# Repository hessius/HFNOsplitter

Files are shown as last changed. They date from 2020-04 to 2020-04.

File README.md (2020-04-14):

# Welcome to the HFNOsplitter project - SHFNO.org

This project is dedicated to doubling the capacity for High Flow Nasal Oxygen (HFNO) treatment by simultaneously connecting two COVID-19 patients to one HFNO-device by adding 3D printed parts.
We also provide thorough medical instructions, validation, and risk analysis to enable other healthcare providers to adopt Split HFNO (SHFNO).
This project is currently only aimed at the Airvo™ 2 Optiflow™ system (Fisher & Paykel Healthcare Limited, Berkshire, United Kingdom).

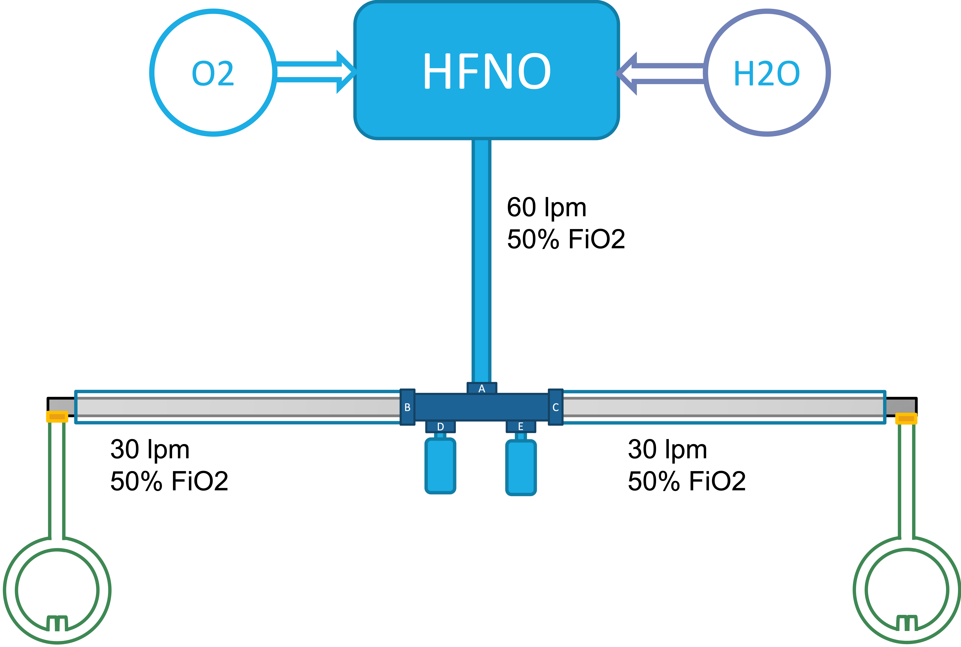
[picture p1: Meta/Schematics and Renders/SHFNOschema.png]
SHFNO Schematic setup

_Fig 1. SHFNO Schematic setup_

**N.B. 1 This solution is provided as is with no express or implied warranty.** [**_Provided under the CERN-OHL-S license_**](https://github.com/hessius/HFNOsplitter/blob/master/LICENSE_cern_ohl_s_v2.pdf).
**In no event will the authors be held liable for any damages arising from the use of this solution.** [**_Legal notice_**](Documentation/en/00%20about%20this%20documentation.html).

**N.B. 2 This project is not done in conjuction or collaboration with, nor under the influence of the original manufacturer of any equipment, medical or otherwise.**

---

## Working group

- **Jesper Hessius**

  - _MD, Internal Medicine and Cardiology Resident_, Västmanland Hospital Västerås Region Västmanland
  - **Role:** Project initiator - Project coordinator - Documentation - Risk analysis

---

- **Erik Cederberg**

  - _Chief Engineer_, 3Dverkstan
  - **Role:** CAD - Design

---

- **Erik Ekbom**

  - _Biomedical Engineer_, Imaging and Functional Technology, Skåne University Hospital Lund
  - **Role:** 3D printing

---

- **Petter Frieberg**
  - _MD, Engineer, PhD-Student_, Clinical Physiology and Nuclear Medicine, Skåne University Hospital Lund
  - **Role:** Validation - Flow simulations

---

- **Einar Heiberg**
  - _Associate Professor, Engineer_, Clinical Physiology, Skåne University Hospital Lund
  - **Role:** 3D printing - Regulatory affairs

---

- **Per Nordqvist**
  - _Biomedical Engineer_, Department of Medical Technology Skåne<br> Region Skåne
  - **Role:** Regulatory affairs - Documentation - Risk analysis

---

- **Göran Petersson**
  - _Biomedical Engineer_, Department of Medical Technology Skåne<br> Region Skåne
  - **Role:** Validation - Documentation

---

## Thanks to

### [3Dverkstan](http://3dverkstan.se) for providing their time, effort, expertise and printers for this project. Without them none of this would have happened.

All the online communities, doctors, nurses and medical technicians who have provided their input and knowledge into every step of this process.

---

## License

**[Provided under the CERN-OHL-S license](https://github.com/hessius/HFNOsplitter/blob/master/LICENSE_cern_ohl_s_v2.pdf).**

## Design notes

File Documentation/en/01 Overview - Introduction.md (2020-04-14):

# Overview

Treating two patients in parallell with High-Flow Nasal Oxygen (HFNO) using the Airvo 2 system is possible due to<br>
a. Treatment guidelines that stipulate a maximum flow should be kept as low as possible to avoid / minimise aerosol dispersion, often capped at 30 lpm.<br>
b. The Airvo 2 system being capable of outputting 60 litres/minute (well above recommended maximum air flow)

Treating two patients in parallell with HFNO using the Airvo 2 system is feasible due to<br>
a. Unidirectional high flow makes cross contamination unlikely<br>
b. Using this only for cohort care with patients with the same disease makes cross contamination less significant<br>
c. HFNO being a completely open system / circuit makes patient factors non significant for air flow dynamics<br>
d. In the authors' limited experience the COVID-19 patients are often titrated to very similar treatments<br>

---

# Basic Schematics

| Standard Setup                                                                                     | SHFNO setup                                                                         |
| -------------------------------------------------------------------------------------------------- | ----------------------------------------------------------------------------------- |
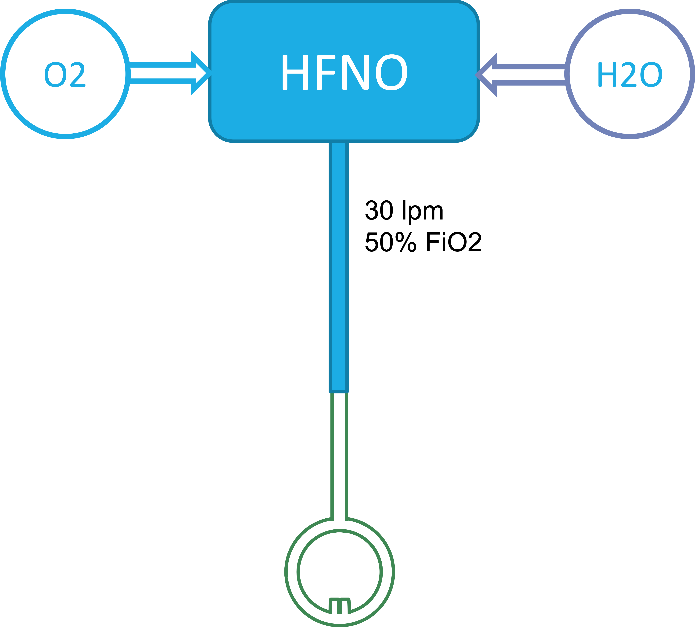
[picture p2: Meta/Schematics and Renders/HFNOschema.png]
Standard HFNO Setup
|  | SHFNO Setup |

---

# Introduction

High-Flow Nasal Oxygen (HFNO) / High Flow Nasal Cannula (HFNC) is a staple of treatment in COVID-19, especially as many countries, regions, hospitals, and health care providers are now recommending against regularly using CPAP and Non-Invasive Ventilation (NIV)/BiPAP in these patients. This is the case in Sweden (where this project was initiated), where the Infectious Diseases Association of Sweden (**IDAS**, "Svenska Infektionsläkarföreningen" in Swedish) has recommended not using CPAP or NIV as well as limited upper maximums for HFNO (See below).

In the best case scenario, used in a timely and correct manner in the context of the COVID-19 pandemic, HFNO/HFNC can be used to avoid intubation and invasive ventilation. However, access to HFNO systems can be severely limited and scarcer than other equipment such as BiPAP machines.

The main system in use outside of the ICU is the Fisher & Paykel Airvo 2, often called "**Optiflow**", which more precisely is the special nasal cannula used with the system. The Airvo is capable of outputting 2-60 litres / minute of airflow with 21-100% FiO2 and uses wholly proprietary connectors which are not readily available and cannot be used with standardised respiratory equipment.

IDAS, as well as the [Karolinska University Hospital](https://strummet.files.wordpress.com/2020/03/pmi-karolinska-covid-19-lungsvikt-intubation-ventilatorbeh-2020-03-19.pdf) both recommend limiting the HFNO air flow in COVID-19 patients to 30 litres / minute due to risk of aeorosolisation and the FiO2 to 50 % due to the risk of alveolar collapse. Some hospitals, like Västmanland Hospital Västerås (where this project orginated), have subsequently modified these guidelines based on clinical experience to allow higher FiO2 as well as in some cases higher air flows. Even so, **the Airvo 2 is _theoretically_ capable of supplying two patients with HFNO without impeding the maximum recommended levels of treatment** according to major guidelines.

HFNO systems are well suited for split airflow, substantially more so than invasive ventilators, CPAP, or BiPAP. This is due to the open nature of the system, which causes patient factors, such as airway resistance to have minimal impact on the air flow. The unidirectionality of the air flow means that no air is shared between patients, even without added filtration. Even so, it is the authors' suggestion that the only patients eligible for treatment with Split HFNO (Hereon "**SHFNO**") are patients suffering from the same disease, such as COVID-19, which also means that potential cross-bcontamination across patients is less significant. We further recommend against using SHFNO for patients with _confirmed_ secondary bacterial infections as well as for carriers of drug-resistant bacteria.

**While every health care provider utilising SHFNO will need to ensure that they have medical instructions for use in place, these guidelines are provided as an example, which is subject to change and without any liability (_[see Legal Disclaimer](00%20about%20this%20documentation.html)_). These examples are based on the medical instructions for use from Västmanland Hospital Västerås, in Sweden where the project originated.**

In the limited clinical experience of the authors, COVID-19 patients treated under the recommendations above are invariably using HFNO titrated to very similar flows and FiO2. For suggestions on how to start treatment with HFNO / SHFNO please see the provided on [**Setup and Treatment**](04%20setup%20and%20treatment.html).

### To enable SHFNO we provide 3D models of

1. A **T-shaped connector** used to connect the distal end of the Airvo connected tube (AirSpiral) with two standard 22mm CPAP/BiPAP tubes as well as two bottles used to collect condensate.
2. An **Adapter** between the distal end of a standard 22mm CPAP/BiPAP tube and the proximal end of the Optiflow nasal cannula.

**A standard SHFNO setup requires one T-shaped connector as well as two adapters.**

It is our recommendation that these models be printed using high quality resin approved for medical use. Please see part 3 of this documentation, [**Models and Instructions**](03%20models%20and%20instructions.html) for more details.

_Aside from the main set provided are also models of plugs for the B/C, D/E ports as well as other adapters and an alternate T-shaped connector enabling the proprietary connectors to connect to other standardised connectors as setup might differ across hospitals._

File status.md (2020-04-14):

# Status / Progress

This is an ongoing project. In order to correctly prioritise we need your feedback. Please [reach out](contact.html) with any feedback, requests or questions.

### Finished

- Develop solution
- Risk assessment
- Medical instructions (Swedish)
- Medical instructions (English)
- Validation of prototypes
- First clinically aimed production
- Initial roll out (_First standby usage 2020-04-09_)

---

### Ongoing

**Secondary validation**<br>
Further flow rate simulations (aiming for final results mid-april)
Direct flow rate measurement (aiming for initial results mid-april)

**Design tweaking**<br>
Introduction of (optional) distal resistance to decrease importance of resistance introduced by e.g. condensation. Initial designs are done and will now be thoroughly simulated and then brought into testing with direct flow rate measurement.

---

### Pending

- Adaptation to other systems?

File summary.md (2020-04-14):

# Summary

HFNO is a valuable treatment in the ongoing COVID-19 pandemic. Its importance has risen as many healthcare systems now discourage using more readily available Non Invasive Ventilation (e.g. BiPAP). Access to HFNO is severely limited. Treatment guidelines for COVID-19 now stipulate maximum treatment levels of 30 litres / minute. The popular HFNO device Airvo™ 2 ("Optiflow") has a maximum capacity of 60 litres / minute but uses only proprietary connectors and cannot be connected to other devices.
**The basic premise of this project is to provide 3D-printable parts to be able to split the Airvo™ 2 HFNO air flow to enable the system to treat two patients simultaneuosly, thus doubling the treatment capacity.** This should not be used if _**any**_ other method of providing HFNO exists!

This project provides both the 3D-models of parts needed for split HFNO treatment as well as _**suggested**_ instructions for use and manufacturing instructions. We also aim to continuously provide the validation from both simulations / calculations as well as real world usage.

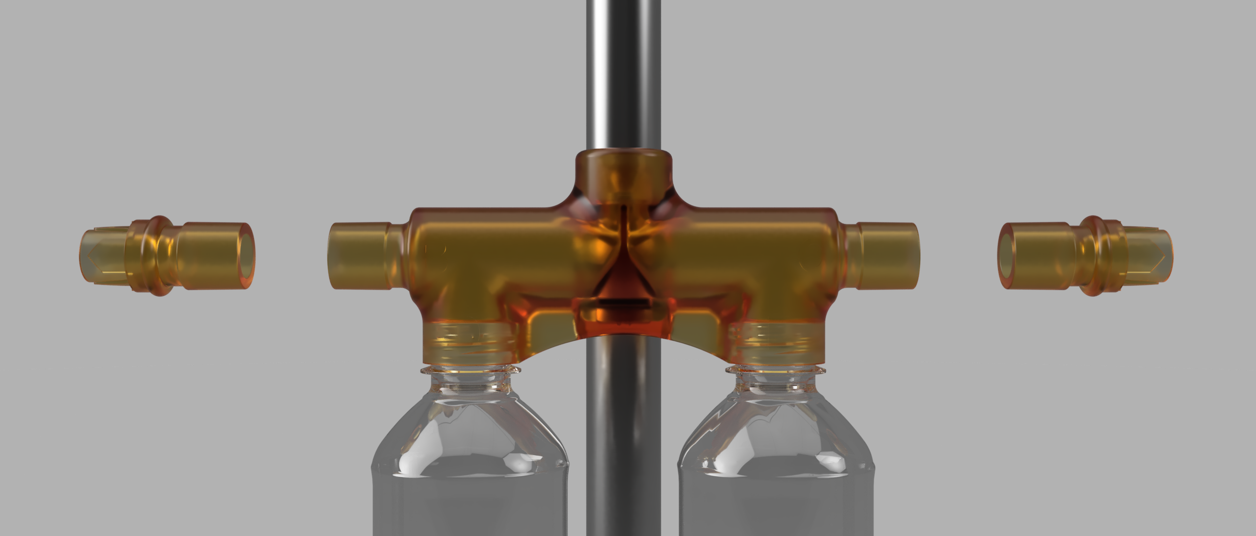
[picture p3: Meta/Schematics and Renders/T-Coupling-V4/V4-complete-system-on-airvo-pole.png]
Render of T-Shaped Connector Render of setup

_Fig 1. Render of the T-shaped connector and adapters that enable SHFNO_

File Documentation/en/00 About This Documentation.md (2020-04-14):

# About This Documentation

This documentation is provided as is, and in no event will the authors be held liable for any damages arising from the use of this material and instructions.

With that said, we have undertaken a lot of work to try to make this desperate measure as safe as possible. Both the designs and documentation have been put through several iterations to try to optimize clarity, ease of use, safety and reproducibility.

We therefore ask for your help - If you find anything that you object to or think could be improved, please share so that we can continually improve this project!

This project started at the Västmanland Hospital Västerås in the city of Västerås in Sweden. At its core, this documentation is an adaptation of the instructions for use developed in Västerås. Thus, we will not be held responsible for any damages, liability that result from utilization of this document within other contexts.

Please read through the whole documentation as every section contains information pertinent to the safety of use of the product.

Healthcare systems around the world now face an unprecedented challenge with the COVID-19 pandemic. Best case scenario, in your healthcare system you will not need this. So we are keeping our fingers crossed that this project is not used. But in the case that your system is already at capacity, we sincerely hope that this project might help bring care to more people who are critically ill.

Sincerely

_Jesper Hessius_, MD

# Legal Disclaimer

The material and information contained in this document is for general information purposes only. You should not rely upon the material or information within this documentation as a basis for making any business, legal, medical or any other decisions.

Whilst we endeavor to keep the information up to date and correct; the authors, affiliates, and partners make no representations or warranties of any kind, expressed or implied about the completeness, accuracy, reliability, suitability, or availability with respect to the information, products, services referenced within this documentation or development of any products, services as a result of utilizing this documentation. Any reliance you place on such material is therefore strictly at your own risk. Any action you take upon the information with this documentation is strictly at your own risk and we will not be liable, in any way whatsoever, for any losses, damages, harms, material or otherwise, in connection with use of our document.

You should take all steps necessary to ascertain that this information is correct and safe and to validate this information prior to use.

The information in this document is intended solely for non-commercial use of the user who accepts full responsibility for its use. While we have taken every precaution to ensure that the content of the document is both current and accurate, errors can occur.

The authors, affiliates, and partners assume no responsibility or liability for any errors or omissions in the content of this document or for any errors or omissions that result from the development of any products, services as a result of utilizing this documentation. The information contained is provided on an “as is” basis with no guarantees of completeness, accuracy, usefulness or timeliness.

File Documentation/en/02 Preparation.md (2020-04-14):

# Preparation

In order to start SHFNO treatment, you need to produce the supplied 3D models (see next part of the documentation) and also establish treatment guidelines, indications and contraindications, etc. specific to your practice setting.
The examples provided in this documentation are provided as a guidance (_[see Legal Disclaimer](00%20About%20This%20Documentation.html)_). This guidance may change over time as our experience with SHFNO grows. Also, please bear in mind that some details may be highly healthcare system specific.

### Basic Guidelines

Any form of HFNO treatment is prescribed by the treating physician.
Administration is based on local recommendations and guidelines (including adaptations of this document).

The nurse or respiratory technician administering HFNO treatment is responsible for matching patients, however, all SHFNO treatments need to be approved by the treating physician.

In COVID-19 the target O2 saturation for otherwise healthy individuals is 92-96 %, whereas in individuals with COPD or other risk factors for CO2 retention the target saturation is 88-92 %.

In COVID-19 the maximum treatment levels are are often set to 30 litres / minute of airflow and FiO2 of 50%.

**It is strongly recommended that individual institutions and physicians that attempt to use this documentation to provide SHFNO to patients as a last resort, develop a written informed consent for use identifying potential benefits of therapy, risks, possible complications and alternatives to treatment to be used with patients and/or their appointed representatives/surrogate decision-makers who will use this therapy. This consent should be signed prior to use. Written consent should be obtained in addition to informed consent discussions with patients and/or their appointed representatives/surrogate decision-makers, so patients understand and agree to the risks of utilizing the treatment described.**

### Indications for SHFNO

Include that all of the following criteria are met:

- Patient has indication for HFNO in COVID-19.\*
- Patient lacks contraindication for HFNO.†
- Patient lacks contraindication for SHFNO.
- _**No other method of supplying HFNO is currently possible.**_

\*_For example: Significant hypoxaemia despite maximal oxygen therapy using standard nasal cannulae or reservoir masks. Refer to your current guidelines regarding HFNO use._

†_Refer to your current guidelines_

### Contraindications for SHFNO

If any of the following criteria are met:

- Patient has contraindication for HFNO.‡
- Patient has a _confirmed_ secondary bacterial infection.
  - N.B. Empiric antibiotic treatment does not necessessarily constitute contraindication.
- Patient is a known carrier of drug resistant bacteria.
  - N.B. Screening is not required to be eligible for SHFNO.

‡_Refer to your current guidelines_

### Patient Selection Criteria

The patients meet, or are expected to meet, all of the following criteria:

- Roughly equal in body size.
- Use the same size Optiflow cannula.
- In cohort care or can be transferred to cohort care setting.
- Similar treatment requirements.
  - Patients need to be able to sustained on HFNO treatment with a maximum flow of 30 lpm
  - When needing to start a new patient on SHFNO/HFNO when all Airvo 2 systems are in use, we recommend matching patients with ongoing HFNO treatment with the same or similar settings so that new patients whenever possible can be started on discrete HFNO until requirements for that patient are identified.

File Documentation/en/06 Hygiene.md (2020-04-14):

# Hygiene

**Water chamber** and **AirSpiral tube** are changed every 14 days, if treatment for both patients is stopped or earlier if needed.

**CPAP/BiPAP tube** and **Optiflow nasal cannula** are both patient specific and changed every 14 days, or earlier if needed. Nasal cannulae should be cleaned daily.

**T-connector** is changed when one or both SHFNO patients are changed, after 7 days or earlier if needed. Please note that when transitioning SHFNO to HFNO and back again with a new patient, the T-connector should be changed. The T-connector is cleaned and reused. The T-connector is cleaned by autoclave according to Table 1 below, or by manual wash and at least 5 minutes submersion in alcohol-based surface disinfectant.

**Adapter** is changed when treatment is stopped for that patient, after 7 days or earlier if needed. The adapter is cleaned and reused. The adapter is cleaned by autoclave according to Table 1 below, or by manual wash and at least 5 minutes submersion in alcohol-based surface disinfectant.

**Collection bottle** is changed when treatment is stopped for that patient, after 7 days or earlier if needed. The bottle is cleaned and reused. The bottle is washed manually, the plastic does not tolerate the temperature acheived when autoclaving.

**Airvo 2** is cleaned according to local guidelines and self-cleaning routine when stopping treatment, after 7 days or earlier if needed. If a need for cleaning arises during ongoing treatment, stop airflow, move the water chamber first, then disconnect the proximal end of the AirSpiral and move over to the new system. The rest of the connections are kept intact. Start treatment on the system with the same settings as the previous Airvo 2 system. After starting treatment again, the T-connector can be moved to the new pole stand.

### Autoclave recommendations for adapter and T-connector

| Temperature | Duration   |
| ----------- | ---------- |
| 121 °C      | 15 minutes |
| 138 °C      | 3 minutes  |

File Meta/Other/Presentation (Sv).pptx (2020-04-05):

## Slutsats

Kapacitet Airvo 2 (Optiflow)
Maximalt flöde 60 l / min

Behandlingsriktlinjer SILF
Maximalt flöde 30 l / min
Maximal FiO2 50 %

Optiflow vid COVID-19

En Optiflow-maskin (Airvo 2) skulle teoretiskt kunna stödja 2 patienter vid max-behandling utan inskränkning i behandlingen och sjukvårdens kapacitet för Optiflow skulle således kunna dubbleras utan leverans av ytterligare system vilket för närvarande är omöjligt.

Projekt: Dubblerat flöde

## Projekt: Dubblerat flöde

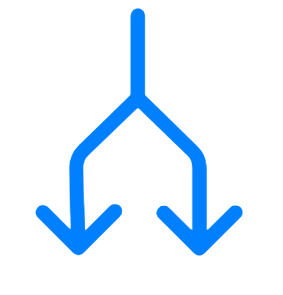
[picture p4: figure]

Jesper Hessius, ST-läkare, Medicinkliniken Västerås

2020-04-01

## Standardkoppling

O2

H2O

HFNO

30 lpm
50% FiO2 (15 lpm)

Projekt: Dubblerat flöde

## Delad koppling

O2

H2O

HFNO

60 lpm
50% FiO2 (30 lpm)

B

A

C

D

E

30 lpm
50% FiO2 (15 lpm)

30 lpm
50% FiO2 (15 lpm)

Projekt: Dubblerat flöde

## Delad koppling

Syrgasaggregat
- Finns med olika kapacitet
- För att uppnå rek max (50% FiO2 vid 60 lpm) krävs 0-30l

O2

H2O

AirSpiral™ Tube
- Uppvärmd luftslang (mot kondens)
- Specifikationer
  - 1.2 m l
  - 22 mm diameter
  - Värms med kopparslinga
  - Proprietära kopplingar

HFNO

Airvo™ 2
- De facto standard för HFNO i Sverige
- I folkmun ”Optiflow”
- Levererar syresatt uppvärmd fuktad luft
  - FiO2 21-100%
  - Flöde 2-60 lpm

Philips Respironics BiPAP /
CPAP Reusable Flexible Tubing.
- Standard-CPAP-slang
- Specifikationer
  - 1.8 m l
  - 22 mm diameter
  - Standardiserad koppling

B

A

C

D

E

Philips CPAP-Slangisolator
- ”Slangstrumpa”
- Passiv isolering
- Hjälper att bibehålla temperatur och minska kondens
- Inte strikt nödvändig (ej begränsande)

T-koppling
- Från: Distal AirSpiral
- Till: Standardiserad koppling och vätskeuppsamlingsflaska

Optiflowadapter
- Från: Standardiserad koppling
- Till: Proximal Optiflow

Optiflow™ Nasal Cannula
- Semipermeabel slang för att motverka kondens
- I distala änden finns högflödesgrimma
- Proprietär koppling (proximalt)

Projekt: Dubblerat flöde

## Delad koppling

B

A

C

D

E

O2

H2O

HFNO

B

A

C

D

E

Projekt: Dubblerat flöde

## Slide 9

B

A

C

D

E

AirSpiral

CPAP / BiPAP

CPAP / BiPAP

Bottle

Bottle

Projekt: Dubblerat flöde

B

A

C

D

E

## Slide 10

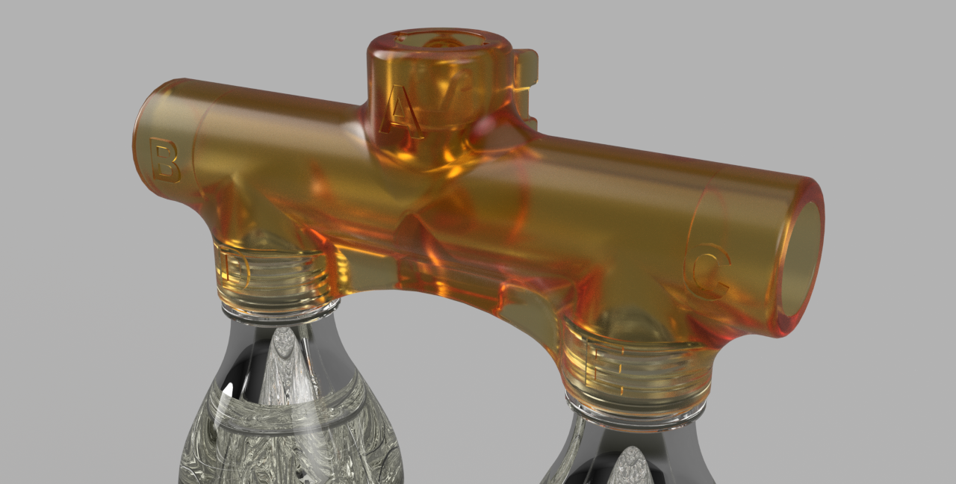
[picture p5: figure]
En bild som visar inomhus, bord, flaska, sitter Automatiskt genererad beskrivning

Projekt: Dubblerat flöde

## Från idé till prototyp!

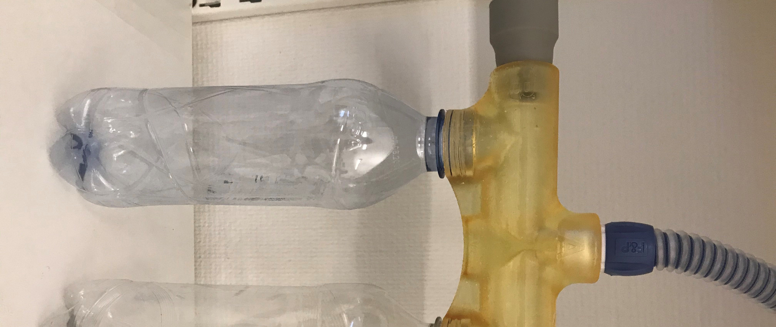
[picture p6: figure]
En bild som visar inomhus, flaska, bord, diskho Automatiskt genererad beskrivning
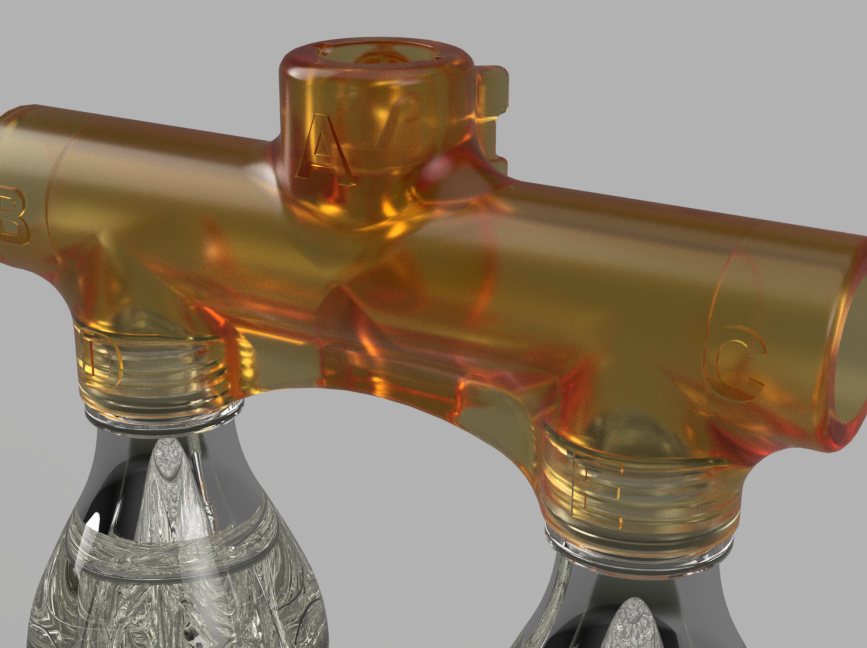
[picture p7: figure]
En bild som visar inomhus, bord, flaska, sitter Automatiskt genererad beskrivning

Projekt: Dubblerat flöde

## Delad koppling

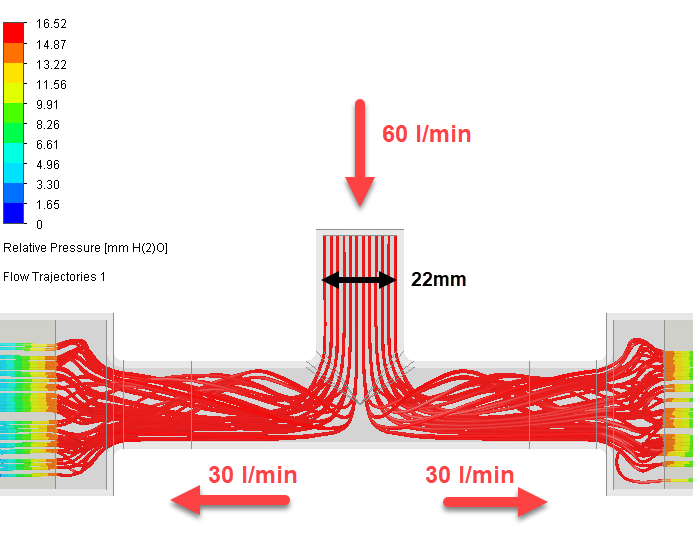
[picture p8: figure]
Förhandsgranskning av bild

Flödessimulering gjord med HME-Filter med specificerat motstånd 1,6 cm H2O vid 30 lpm.
Bekräftar den teoretiska kapaciteten och visar jämnt distribuerat flöde mellan patienterna utan relevant motstånd skapat av filter eller ökad slanglängd.
OBS att filter inte används i den färdiga lösningen

Projekt: Dubblerat flöde

## Första prototyp 29/3

- Optiflow för första gången någonsin(?) ihopkopplad med CPAP-slang!

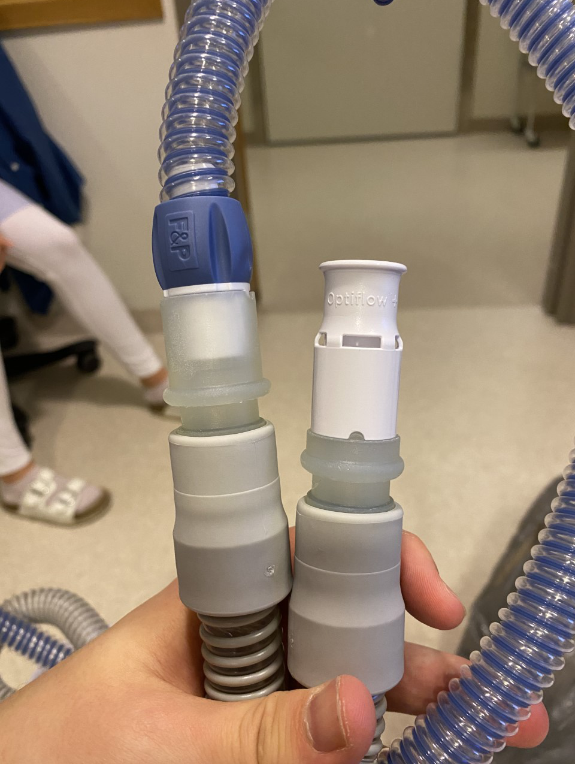
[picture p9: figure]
Förhandsgranskning av bild

Projekt: Dubblerat flöde

## Tidsplan

- Framtagande av lösning: Klar
- Riskanalys: Klar
- Medicinsk instruktion: Klar
- Validering av prototyp: Pågår
- Produktion: Redo att starta 7/4
- Införande: Start av beredskap för behandling med delad Optiflow 8/4

Projekt: Dubblerat flöde

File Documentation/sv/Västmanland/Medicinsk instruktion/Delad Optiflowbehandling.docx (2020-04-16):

Instruktion: Delad Optiflowbehandling

INLEDNING
Behandling med högflödessyrgasgrimma (HFNO – High Flow Nasal Oxygen / HFNC – High Flow Nasal Cannula) är en avgörande behandling vid COVID-19, om rätt använt och i rätt tid kan man i bästa fall undvika ventilatorbehandling. Tillgången till dessa system är dock kraftigt begränsad. Den vanligaste maskinen för HFNO använder heter "Airvo 2" och benämns oftast ”Optiflow” efter den grimma som används i systemet. I detta dokument benämns behandling med högflödesgrimma i allmänhet som ”HFNO” och behandling med Airvo 2 som Optiflow medan själva apparaten som producerar luftflödes benämns ”Airvo”

För bakgrund, indikation och inställningar av Optiflowbehandling i intermediärvårdsmiljö hänvisas till dokument 38605-2 ”Optiflowbehandling på MIMA” i ledningssystemet.

Särskilda riktlinjer för behandling av patienter med COVID-19 är framtagna där man utifrån den risk för aerosolbildning vid höga flöden och alveolär kollaps vid höga syrgashalter satt behandlingsgränser långt under Airvo 2-systemens fulla kapacitet. Ett system har därför kapacitet att användas för två patienter.

Denna instruktion för delning av Optiflow är särskilt framtagen för rådande COVID-pandemi och är inte applicerbar utanför en krissituation där triagering av vårdinsatser annars är nödvändig och kan endast användas om ingen annan metod för att behandla patienten med HFNO finns tillgänglig.

För detta ändamål har särskilda adaptrar tagits fram och producerats av Medicinkliniken i Västerås, Region Skåne och företaget 3Dverkstan. Dessa tillhandahålles inte av tillverkaren av Airvo 2. Dessa adaptrar är flergångsföremål som autoklaveras mellan användning (se rubrik Bytes- och Rengöringsrutin). Plasten i dessa adaptrar är godkänd medicinsk produkt och bedöms inte medföra någon risk för patienten.

ANSVAR

Optiflowbehandling ordineras av läkare och administreras utifrån detta PM och PM 38605-2 av sjuksköterska.

Sjuksköterska ansvarar för att identifiera potentiella matchade patienter och delning av Optiflow skall alltid godkännas av ansvarig läkare.

Vid COVID-19 är målsaturation hos tidigare lungfrisk patient 92-96%, hos patient med KOL eller risk för CO2-retention 88-92%.

Vid COVID -19 är för samtliga patienter övre gränsvärde för flöde 45 liter/min (per patient) och FiO2 70%.

FÖRBEREDELSE

Indikation för Optiflowbehandling vid COVID-19
Otillräcklig effekt av syrgasbehandling med grimma eller reservoarmask.

Indikation för delad Optiflowbehandling
Uppfyller samtliga av

- Uppfylld indikation för Optiflowbehandling vid COVID-19
- Avsaknad av kontraindikation för Optiflowbehandling
- Avsaknad av kontraindikation för delad Optiflowbehandling
- Ingen annan möjlighet finns för att ombesörja HFNO

Kontraindikation för Optiflowbehandling
Se dokument 38605-2

Kontraindikation för delad Optiflowbehandling

- Konstaterad sekundär bakteriell infektion
  - Observera att empirisk antibiotikabehandling inte med nödvändighet utgör kontraindikation
- Känt bärarskap av multiresistent bakterie

Matchning av två patienter
Patienterna uppfyller, eller kan förväntas uppfylla, samtliga av följande

- Ungefärlig jämnstor kroppshydda
- Använder samma storlek på Optiflowgrimma (se 38605-2)
- Samvårdas eller kan samvårdas
- Kan uppnå och upprätthålla satta behandlingsmål med flöden på 30lpm eller lägre.
- Liknande behandlingsbehov
  - Vid behov av nystart av patient, utan tillgång till maskin, bör man i första hand matcha patienter med pågående enskild behandling med samma el. liknande inställningar för att kunna utföra nystart med enskild behandling om möjligt.

Utrustning

- Fisher & Paykel Airvo 2.
- Stativ med Airvo 2 samt syrgasblandare.
- Befuktningskammare.
- 1 x Slangset Fisher & Paykel AirSpiral
- 2 x Näsgrimma Fisher & Paykel Optiflow
  - OBS! Bägge grimmor måste vara identiska
- 2 x CPAP/ BiLevel-slang
  - 22 mm diameter och 1,8 m längd
  - Ex. Philips Respironics BiPAP / CPAP Reusable Flexible Tubing
  - OBS! Bägge slangar måste vara identiska
- (Valfritt efter tillgång: 2 x Philips Slangisolator – ”Slangstrumpa”)
- T-formad delningsadapter, märkt ABCDE – ”T-koppling”
- 2 x Mindre delningsadapter (22mm – Optiflow) – ”Adapter”
- 2 x Rengjord 50 cl PET-flaska – ”Uppsamlingsflaska"
- 2 x Buntband (minst 10 cm längd)
- 1 x Engångspropp / Flergångspropp – Används endast om start med enskild behandling med koppling förberedd för delning, se nedan)
- Baxter Sterilt vatten 1000 ml.
- Inplastad snabbguide.

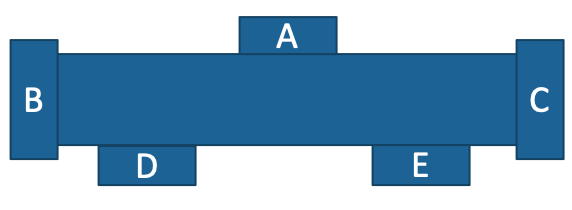
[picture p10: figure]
En bild som visar skärm, klocka, TV, spelare Automatiskt genererad beskrivning

Fig 1. Schematisk bild ”T-koppling”

Uppkoppling

Observera att snabbguide fäst vid maskinen endast visar koppling för enskild patient med standard och inte redogör för delad Optiflowbehandling eller enskild behandling med förberedd delbar koppling.

1. Anslut (skruva fast) två tomma uppsamlingsflaskor till kopplingar på T-kopplingens undersida, märkt D och E (passar endast där).
2. T-kopplingens monteras på stativet för Airvo 2 strax ovan Airvo 2 (nedanför patienthöjd). T-kopplingen skall vara orienterad så att PET-flaskor pekar nedåt. T-kopplingen kan monteras i standardfäste (”IVA-skena”) eller med buntband.
  a. Buntband: Sätt T-kopplingens konkava yta mot Airvo-stativets stång. Fäst T-kopplingen mot stången med 2 buntband som träs genom hällorna på T-Kopplingen.
  b. IVA-skena: Montera T-kopplingen i IVA-skena på Airvo-stativet. Vid behov kan T-kopplingen monteras i annan IVA-skena, exempelvis väggmonterad, observera att denna måste vara monterad lägre än patientsängens huvudända!
3. Förbered befuktningskammaren genom att ta bort de blå locken och anslut de medföljande kopplingsrören. Sätt befuktningskammaren på plats i apparaten, se till att den klickar i ordentligt.
4. Anslut slangen från befuktningskammaren till påsen med sterilt vatten.
5. Anslut AirSpiral-slangen till kopplingen ovanpå Airvo (passar bara åt ett håll) och fixera med den blå låsringen.
6. Koppla den distala änden av AirSpiral-slangen till kopplingen på T-kopplingens ovansida, märkt A (passar endast där). Slangen kan om möjligt hängas över dropp-ställning överst på stativet, då kan kondens från ena sidan rinna tillbaka till Airvo-systemet och från den andra till uppsamlingsflaskorna.
7. Koppla CPAP/BiLevel-slang på de två kvarvarande kopplingarna på T-kopplingen (märkta B och C)*
8. (Vid tillgång till slangstrumpa bekläd respektive CPAP/BiLevel-slang med slangstrumpa)
9. Koppla Adapter på andra änden av respektive CPAP/BiLevel-slang
10. Koppla Optiflowgrimma till respektive adapter
11. Koppla in syrgasaggregatet i uttaget för syrgas i väggpanelen.
12. Klart för start!

*Vid start av enskild behandling med förberedd koppling proppas ena sidan, B eller C med propp och den andra kopplas enligt instruktion ovan. Observera att bägge uppsamlingsflaskor behövs eller propp även för flaskan på den tomma sidan!

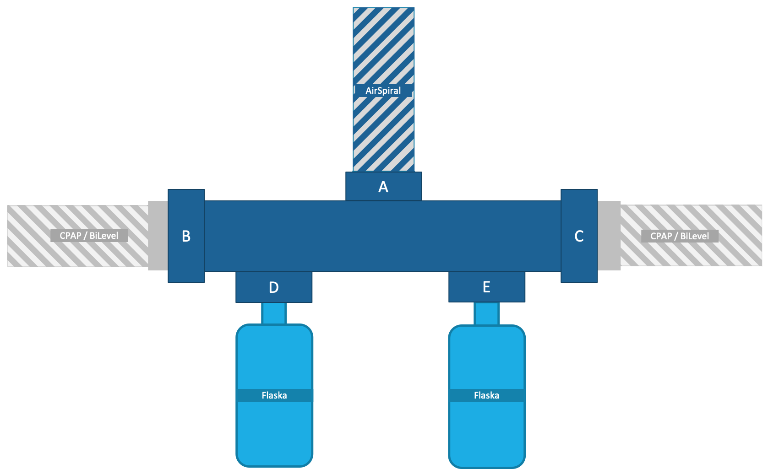
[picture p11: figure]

Fig 2. Schematisk bild över kopplingsschema

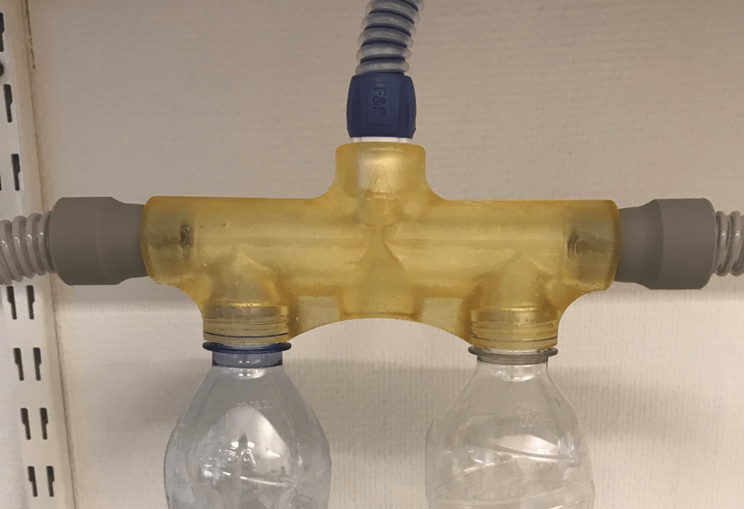
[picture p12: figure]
En bild som visar inomhus, vatten, flaska, bord Automatiskt genererad beskrivning

Fig 3. Bild på kopplad T-koppling

UTFÖRANDE

Start av delad behandling

- Luftflöde startas på 60 liter / min i Airvo 2-systemet vilket levererar 30 liter / min till respektive patient.
- FiO2 startas på 50% i Airvo 2-systemet vilket levererar 50 % till respektive patient.
  - OBS! FiO2 titreras som vanligt och syrgasinnehållet är lika för bägge patienter som i Airvo 2-systemet.
- Ställ temperaturen på 37° C. Vid behov sänks temperaturen till 34° C.
- Titrera FiO2 för att hålla bägge patienter inom målsaturation.
  - Vid svårighet att matcha FiO2 som håller bägge patienter inom målsaturation kan man vid behov lägga sig på den nivå som är lägst av de två patienternas och koppla oxymask över Optiflow över den andre patienten och titrera till målsaturation, OBS att detta endast ska gälla vid små diskrepenser och inget stort flöde skall ges i Oxymask på detta vis, detta då vi får sämre kontroll på FiO2.

Start av enskild behandling med förberedd koppling

- Koppla enligt rutin fram till T-stycke.
- Proppa tom sida med röd propp.
- Koppla därefter patientsidan enligt rutin ovan.
- Luftflöde startas på 30 liter / min i Airvo 2-systemet.
- FiO2 startas på 50% i Airvo 2-systemet.
- Ställ temperaturen på 37° C. Vid behov sänks temperaturen till 34° C.
- Titrera FiO2 för att hålla patienten inom målsaturation.

Övergång från enkel behandling med förberedd koppling till delad behandling

Observera att fuktkammare och AirSpiral-slang inte behöver bytas om koppling varit förberedd för delning.

- Koppla fri CPAP/BiLevel-slang till adapter.
- Koppla Optiflowgrimma till adapter (Kontrollera att det är samma storlek som för den andra patienten i systemet).
- Koppla grimma på patient.
- Ta bort röd propp från T-koppling och koppla på den förberedda CPAP/BiLevel-slangen på T-kopplingen.
- Öka flödet på Airvo 2 till 60 liter / min.
- Titrera upp syrgas till önskad nivå.

Övergång från enkel behandling med standardkoppling till delad behandling

För att minimera tid utan behandling och för försäkra efterlevnad till hygienrutiner bör övergång från enkel behandling med standardkoppling till delad behandling ske genom byte av Airvo 2. Vid övergången kan patientens Optiflowgrimma behållas men fuktkammare och AirSpiralslang kan inte återanvändas.

- Koppla enligt rutin ovan fram till att adapter kopplas på bägge CPAP/BiLevel-slang.
- Ska någon av patienterna startas med delad behandling? Färdigställ då den sidan av kopplingen enligt rutin.
- Koppla över befintlig Optiflow-grimma för den eller de patient(er) som går över från enskild behandling till adapter i det nya delade systemet.
- Följ därefter instruktion ”Start av delad behandling” och titrera till önskad behandlingsnivå

Övergång från delad behandling till enskild behandling (avslut av en patient)

- Kontrollera kondens i slangarna och se till att eventuell kondens rinner tillbaka till uppsamlingsflaskor.
- Stäng av flöde i Airvo 2 och syrgas.
- Koppla ifrån CPAP-slang från T-koppling för patienten som skall avsluta behandling.
- Proppa ledig sida i T-koppling med röd propp.
- Byt uppsamlingsflaska på den berörda sidan (OBS att bägge sidor behöver ha uppsamlingsflaska!).
- Starta enligt rutin ”Start av enskild behandling med förberedd koppling”

Kondens
Var observant på kondens i slangsystemet. Vid delad Optiflowbehandling ökar kondensmängden och vatten kan ansamlas i CPAP/BiLevel-slang.
2 gånger per pass, ca var 4e timme skall CPAP/BiLevel-slang kontrolleras och lyftas på så sätt att kondens rinner tillbaka till T-kopplingen och samlas i uppsamlingsflaskan.

Uppsamlingsflaskan skall tömmas innan den blir helt fylld och behöver inte diskas efter tömning vid fortsatt behandling hos samma patient. Rekommendationen är att skruva ut flaskan och omedelbart hälla över vätskan i ett annat kärl i anslutning till maskinen och därefter skruva tillbaka flaskan. Om detta är omöjligt rekommenderas byte av flaska i samband med tömning och att tom ersättningsflaska skruvas på omedelbart efter att den fulla flaskan skruvas ut, detta då systemet inte kan leverera behandling utan inskruvad flaska.

Om möjligt försök orientera CPAP/BiLevel-slang på så sätt att kondens kontinuerligt kan rinna tillbaka till uppsamlingsflaskan. Observera att CPAP/BiLevel-slang inte får läggas över skiljevägg mellan patienter då kondensen då kommer att rinna till patienten.

Sterilt vatten
Notera att 1000 ml sterilt vatten vid delad behandling räcker kortare än vid enskild behandling då kondens inte återförs till befuktningskammaren. Airvo larmar när befuktningskammaren är torr, se till att byta påsen med sterilt vatten innan den tar slut och befuktningskammaren ”torrkokar”.

BYTES- OCH RENGÖRINGSRUTIN
Befuktningskammare och AirSpiralslang bytes var 14:e dag, om bägge patienters behandling avslutas eller vid behov.

CPAP/BiLevel-slang och Optiflow-grimma är patientbundna. Bytes var 14e dag eller vid behov. Daglig rengöring av näsgrimman.

T-koppling bytes vid byte av ena eller bägge patienterna i delad Optiflowbehandling, efter 7 dagar eller vid behov. T-koppling rengörs efter användning och återanvänds. T-koppling rengörs antingen genom autoklavering enligt nedanstående tabell eller diskning och 5 minuters bad i ytdesinfektion.

Adapter bytes när behandling avslutas för den patienten, efter 7 dagar eller vid behov. Adapter rengörs efter användning och återanvänds. Adapter rengörs antingen genom autoklavering enligt nedanstående tabell eller diskning och 5 minuters bad i ytdesinfektionsmedel.

Uppsamlingsflaska bytes när behandling avslutas för den patienten, efter 7 dagar eller vid behov. Flaskan diskas efter användning och återanvänds. Plasten i flaskan tål inte autoklavering.

Rengöringsrutin av Airvo enligt 38605-2 görs vid avslut av behandling av bägge patienter, efter 7 dagar, eller vid behov. Vid behov av rengöring vid pågående behandling bör annat airvo-system tillgängliggöras och fuktkammare flyttas först över till det nya systemet, därefter AirSpiral-slang. Därefter startas behandling ånyo på samma inställningar som tidigare. Först därefter flyttas T-koppling.

Autoklavering för adapter och T-koppling

Temperatur | Duration
121° C | 15 minuter
138° C | 3 minuter

FELFÖREBYGGANDE, FELSÖKNING OCH FELAVHJÄLPNING
Då denna rutin är framtagen som en nödåtgärd krävs extra försiktighet vid delad Optiflowbehandling. Därför skall ouppackad eller patientbunden reservoarmask alltid förvaras på patientsal hos patient med delad Optiflowbehandling.

Vid patientförsämring under pågående delad Optiflowbehandling gås kontrollrutin igenom steg för steg i tillägg till ordinarie åtgärder.

Kontrollrutin genomförs av ansvarig sjuksköterska minst en gång per pass (i början av passet).

Kontrollrutin

1. Kontrollera grimma Sitter grimman korrekt i näsan? Obs att Airvo-systemets varning för potentiell knickbildning inte fungerar vid delad behandling. Kontrollera att det inte ansamlat kondens i grimmslangen.
2. Kontrollera samtliga kopplingar Börja proximalt och arbeta utåt. Kontrollera att samtliga kopplingar sitter säkert. Vid misstanke om glapp i någon koppling testa att byta adapter eller T-koppling.
3. Kontrollera CPAP/BiLevel-slang Se till att ingen knickbildning finns längs med hela slangen. Kontrollera att det inte ansamlats kondens i slangen.
4. Kontrollera AirSpiral-slang Se till att ingen knickbildning finns längs med hela slangen. Kontrollera att det inte ansamlats kondens i slangen.
5. Kontrollera uppsamlingsflaska Se till att flaskan inte är full och att den är korrekt fastskruvad utan möjlighet till luftläckage.

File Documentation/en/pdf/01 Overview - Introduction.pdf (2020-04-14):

01 Overview - Introduction.md - SHFNO.org | Updated on: 4/14/2020

1 / 2

# Overview

Treating two patients in parallell with High-Flow Nasal Oxygen (HFNO) using the Airvo 2 system is possible due to
a. Treatment guidelines that stipulate a maximum flow should be kept as low as possible to avoid / minimise aerosol dispersion, often capped at 30 lpm.
b. The Airvo 2 system being capable of outputting 60 litres/minute (well above recommended maximum air flow)

Treating two patients in parallell with HFNO using the Airvo 2 system is feasible due to
a. Unidirectional high flow makes cross contamination unlikely
b. Using this only for cohort care with patients with the same disease makes cross contamination less significant
c. HFNO being a completely open system / circuit makes patient factors non significant for airflow dynamics
d. In the authors' limited experience the COVID-19 patients are often titrated to very similartreatments

# Basic Schematics

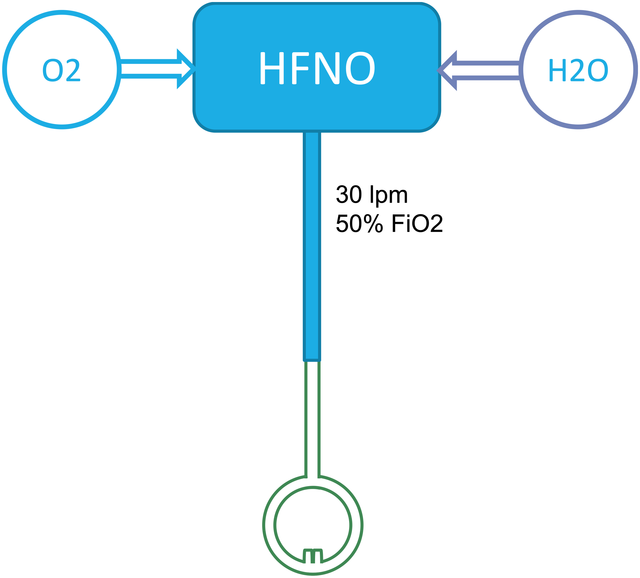
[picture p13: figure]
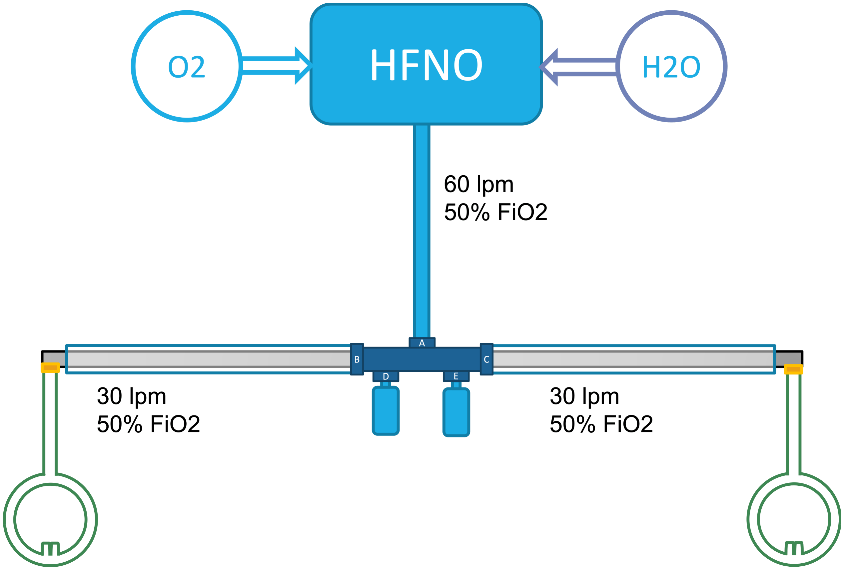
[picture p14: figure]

StandardSetup | SHFNO setup

# Introduction

High-Flow Nasal Oxygen (HFNO) / High Flow Nasal Cannula (HFNC) is a staple of treatment in COVID-19, especially as many countries,regions, hospitals, and health care providers are now recommending against regularly using CPAP and Non-Invasive Ventilation (NIV)/BiPAP in these patients. This is the case in Sweden (where this project was initiated), where the Infectious Diseases Association of Sweden (IDAS, "Svenska Infektionsläkarföreningen" in Swedish) has recommended not using CPAP or NIV as well as limited upper maximums for HFNO (See below).

01 Overview - Introduction.md - SHFNO.org | Updated on: 4/14/2020

2 / 2

In the best case scenario, used in a timely and correct mannerin the context of the COVID-19 pandemic, HFNO/HFNC can be used to avoid intubation and invasive ventilation. However, access to HFNO systems can be severely limited and scarcerthan other equipment such as BiPAP machines.

The main system in use outside of the ICU is the Fisher & Paykel Airvo 2, often called "Optiflow", which more precisely is the special nasal cannula used with the system. The Airvo is capable of outputting 2-60 litres / minute of airflow with 21-100% FiO2 and uses wholly proprietary connectors which are notreadily available and cannot be used with standardised respiratory equipment.

IDAS, as well as the Karolinska University Hospital (https://strummet.files.wordpress.com/2020/03/pmi-karolinska-covid-19-lungsvikt-intubation-ventilatorbeh-2020-03-19.pdf) both recommend limiting the HFNO airflow in COVID-19 patients to 30 litres / minute due to risk of aeorosolisation and the FiO2 to 50 % due to the risk of alveolar collapse. Some hospitals, like Västmanland Hospital Västerås (where this project orginated), have subsequently modified these guidelines based on clinical experience to allow higher FiO2 as well as in some cases higher air flows. Even so, the Airvo 2 is theoretically capable of supplying twopatients with HFNO without impeding the maximum recommendedlevels of treatment according to major guidelines.

HFNO systems are well suited for split airflow, substantially more so than invasive ventilators, CPAP, or BiPAP. This is due to the open nature of the system, which causes patient factors, such as airway resistance to have minimal impact on the airflow. The unidirectionality of the airflow means that no airis shared between patients, even without added filtration. Even so, it is the authors' suggestion that the only patients eligible fortreatment with Split HFNO (Hereon "SHFNO") are patients suffering from the same disease, such as COVID-19, which also means that potential cross-bcontamination across patients is less significant. We furtherrecommend against using SHFNO for patients with confirmed secondary bacterial infections as well as for carriers of drugresistant bacteria.

While every health care provider utilisingSHFNO will needto ensure that they have medical instructions for use inplace, these guidelines are providedas an example, which is subject to change and without any liability (see Legal Disclaimer).These examples arebasedon the medical instructions for use from Västmanland Hospital Västerås,inSweden where the project originated.

In the limited clinical experience of the authors, COVID-19 patients treated underthe recommendations above are invariably using HFNO titrated to very similarflows and FiO2. For suggestions on how to start treatment with HFNO / SHFNO please see the provided on SetupandTreatment.

To enable SHFNO we provide 3D models of

. A T-shapedconnector used to connect the distal end of the Airvo connected tube (AirSpiral) with two standard 22mm CPAP/BiPAP tubes as well as two bottles used to collect condensate.
. An Adapter between the distal end of a standard 22mm CPAP/BiPAP tube and the proximal end of the Optiflow nasal cannula.

A standardSHFNO setuprequires oneT-shapedconnector as well as two adapters.

It is ourrecommendation that these models be printed using high quality resin approved for medical use. Please see part 3 of this documentation, Models andInstructions for more details.

Aside from the main set provided are also models of plugs for the B/C, D/E ports as well as other adapters and

an alternate T-shaped connector enabling the proprietary connectors to connect to other standardised

connectors as setup might differ across hospitals.

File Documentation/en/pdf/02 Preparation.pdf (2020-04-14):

02 Preparation.md - SHFNO.org | Updated on: 4/14/2020

1 / 2

# Preparation

In orderto start SHFNO treatment, you need to produce the supplied 3D models (see next part of the documentation) and also establish treatment guidelines, indications and contraindications, etc. specific to your practice setting. The examples provided in this documentation are provided as a guidance (see Legal Disclaimer). This guidance may change overtime as our experience with SHFNO grows. Also, please bearin mind that some details may be highly healthcare system specific.

Basic Guidelines

Any form of HFNO treatment is prescribed by the treating physician. Administration is based on local recommendations and guidelines (including adaptations of this document).

The nurse orrespiratory technician administering HFNO treatment is responsible for matching patients, however, all SHFNO treatments need to be approved by the treating physician.

In COVID-19 the target O2 saturation for otherwise healthy individuals is 92-96 %, whereas in individuals with COPD or otherrisk factors for CO2 retention the target saturation is 88-92 %.

In COVID-19 the maximum treatment levels are are often set to 30 litres / minute of airflow and FiO2 of 50%.

It is strongly recommendedthat individual institutions andphysicians that attempt to use this documentation toprovideSHFNO topatients as a last resort,developa written informedconsent for use identifyingpotentialbenefits of therapy, risks,possible complications andalternatives to treatment tobe used with patients and/or their appointedrepresentatives/surrogatedecision-makers who will use this therapy.This consent shouldbe signedprior to use.Written consent shouldbe obtainedin addition to informedconsentdiscussions with patients and/or their appointedrepresentatives/surrogate decision-makers, sopatients understandandagree to the risks of utilizing the treatmentdescribed.

Indications for SHFNO

Include that all of the following criteria are met:

Patient has indication for HFNO in COVID-19.*
Patient lacks contraindication for HFNO.†
Patient lacks contraindication for SHFNO.
No other methodof supplying HFNO is currentlypossible.

*For example: Significant hypoxaemia despite maximal oxygen therapy using standard nasal cannulae or

reservoir masks. Refer to your current guidelines regarding HFNO use.

†Refer to your current guidelines

Contraindications for SHFNO

If any of the following criteria are met:

Patient has contraindication for HFNO.‡
Patient has a confirmed secondary bacterial infection.

02 Preparation.md - SHFNO.org | Updated on: 4/14/2020

2 / 2

N.B. Empiric antibiotic treatment does not necessessarily constitute contraindication. Patient is a known carrier of drug resistant bacteria.
N.B. Screening is notrequired to be eligible for SHFNO.

‡Refer to your current guidelines

Patient Selection Criteria

The patients meet, or are expected to meet, all of the following criteria:

Roughly equal in body size.
Use the same size Optiflow cannula.
In cohort care or can be transferred to cohort care setting.
Similartreatmentrequirements.
Patients need to be able to sustained on HFNO treatment with a maximum flow of 30 lpm
When needing to start a new patient on SHFNO/HFNO when all Airvo 2 systems are in use, we recommend matching patients with ongoing HFNO treatment with the same or similar settings so that new patients whenever possible can be started on discrete HFNO untilrequirements forthat patient are identified.

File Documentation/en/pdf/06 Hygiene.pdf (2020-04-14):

06 Hygiene.md - SHFNO.org | Updated on: 4/14/2020

1 / 1

# Hygiene

Water chamber and AirSpiral tube are changed every 14 days, if treatment for both patients is stopped or earlierif needed.

CPAP/BiPAPtube and Optiflow nasal cannula are both patient specific and changed every 14 days, or earlier if needed. Nasal cannulae should be cleaned daily.

T-connector is changed when one or both SHFNO patients are changed, after 7 days or earlierif needed. Please note that when transitioning SHFNO to HFNO and back again with a new patient, the T-connector should be changed. The T-connectoris cleaned and reused. The T-connectoris cleaned by autoclave according to Table 1 below, or by manual wash and at least 5 minutes submersion in alcohol-based surface disinfectant.

Adapter is changed when treatment is stopped forthat patient, after 7 days or earlierif needed. The adapteris cleaned and reused. The adapteris cleaned by autoclave according to Table 1 below, or by manual wash and at least 5 minutes submersion in alcohol-based surface disinfectant.

Collectionbottle is changed when treatment is stopped forthat patient, after 7 days or earlierif needed. The bottle is cleaned and reused. The bottle is washed manually, the plastic does not tolerate the temperature acheived when autoclaving.

Airvo 2 is cleaned according to local guidelines and self-cleaning routine when stopping treatment, after 7 days or earlierif needed. If a need for cleaning arises during ongoing treatment, stop airflow, move the water chamberfirst, then disconnect the proximal end of the AirSpiral and move overto the new system. The rest of the connections are kept intact. Start treatment on the system with the same settings as the previous Airvo 2 system. After starting treatment again, the T-connector can be moved to the new pole stand.

Autoclave recommendations for adapter and T-connector

Temperature Duration

121 °C | 15 minutes
138 °C | 3 minutes

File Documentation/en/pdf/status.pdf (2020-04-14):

status.md - SHFNO.org | Updated on: 4/14/2020

1 / 1

# Status / Progress

This is an ongoing project. In orderto correctly prioritise we need yourfeedback. Please reach out with any feedback,requests or questions.

Finished

Develop solution
Risk assessment
Medical instructions (Swedish) Medical instructions (English)
Validation of prototypes
First clinically aimed production
Initialroll out (First standby usage 2020-04-09)

Ongoing

Secondary validation
Furtherflow rate simulations (aiming forfinalresults mid-april) Direct flow rate measurement (aiming forinitial results mid-april)

Design tweaking
Introduction of (optional) distalresistance to decrease importance ofresistance introduced by e.g. condensation. Initial designs are done and will now be thoroughly simulated and then brought into testing with direct flow rate measurement.

Pending

Adaptation to other systems?

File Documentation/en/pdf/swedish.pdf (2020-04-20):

swedish.md - SHFNO.org | Updated on: 4/20/2020

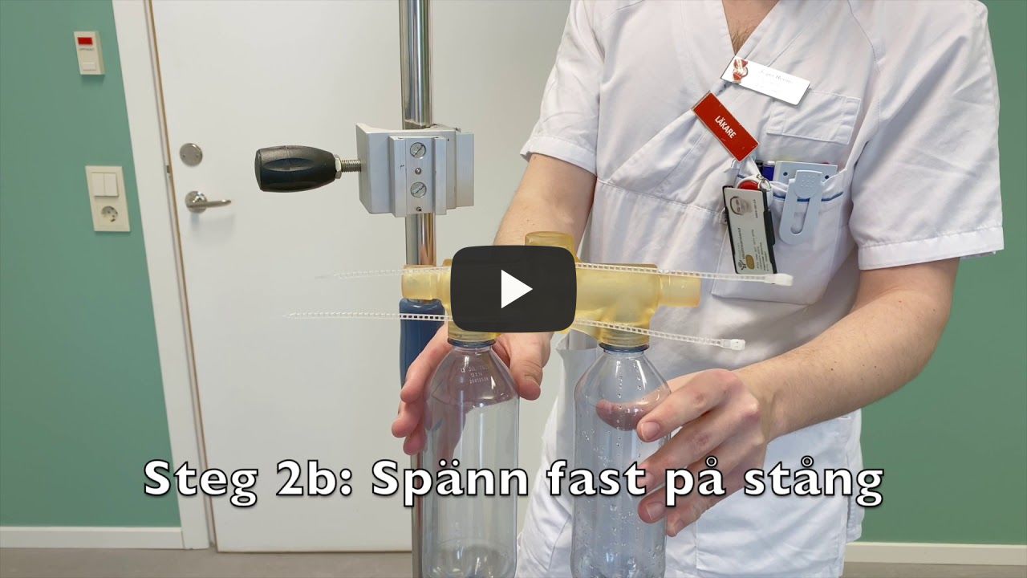
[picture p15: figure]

1 / 1

# Svensk dokumentation

Dokumentation på svenska tillhandahålls i form av de medicinska instruktioner,riskanalys, riskhanteringsschema och produktbeskrivning som tagits fram av och för svenska vårdgivare. Detta gör att det är mycket enkelt att snabbt ta fram den dokumentation som behövs för att ta i kliniskt bruk i svensk kontext i enlighet med SOFS20081 kapitel 5.

Vi har även en mall för den som vill komplettera riskanalys i samband med införande.

Du hittar all dokumentation här (https://github.com/hessius/HFNOsplitter/tree/master/Documentation/sv) eller kan ladda ned den i sin helhet här. (https://yehonal.github.io/DownGit/)

Observera att den svenska dokumentationen inte innehåller detaljerade tillverkningsinstruktioner, för detta hänvisar vi till vår engelskspråkiga dokumentation.

## Videoinstruktion

I denna korta instruktion ser du hur grundkopplingen av delad HFNO-behandling gårtill.

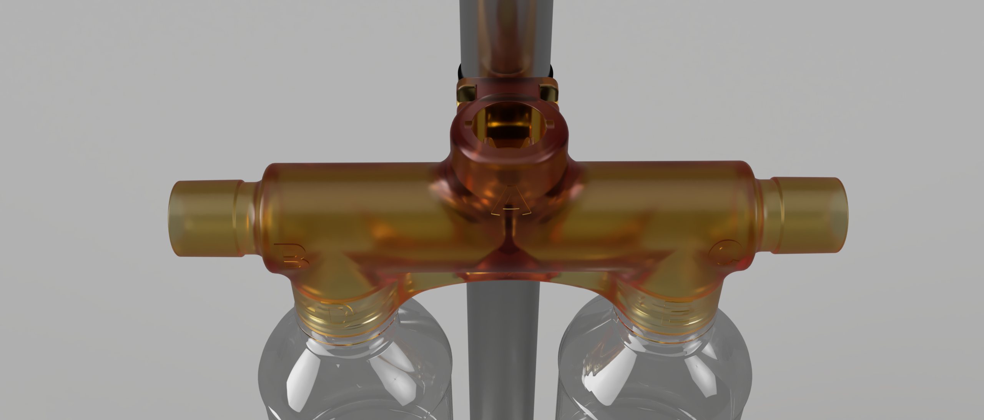
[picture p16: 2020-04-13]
Meta/Schematics and Renders/T-Coupling-V4/V4-on-airvo-pole.png

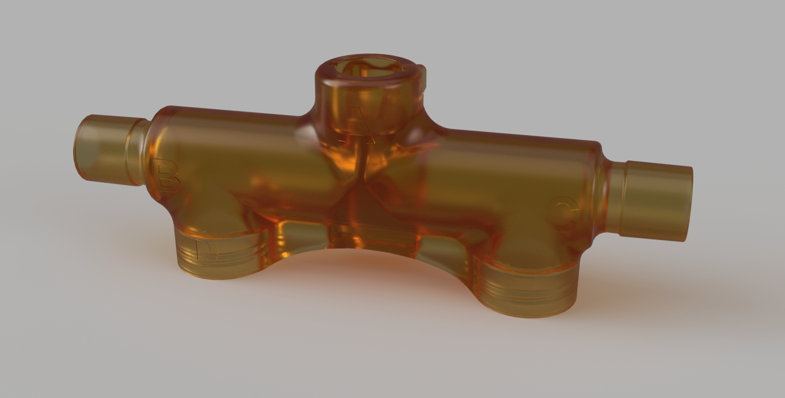
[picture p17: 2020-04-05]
Meta/Schematics and Renders/T-front.png

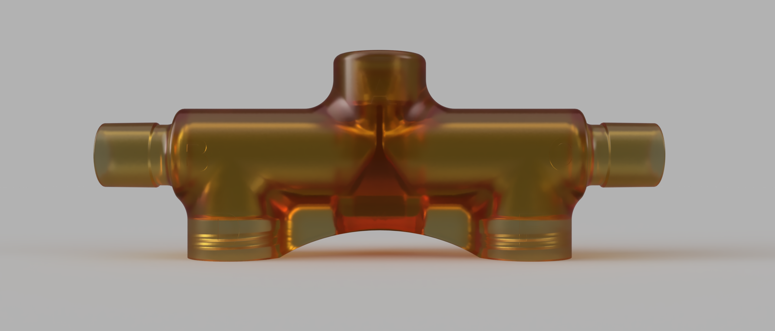
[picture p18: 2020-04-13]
Meta/Schematics and Renders/T-Coupling-V4/V4-front-view.png

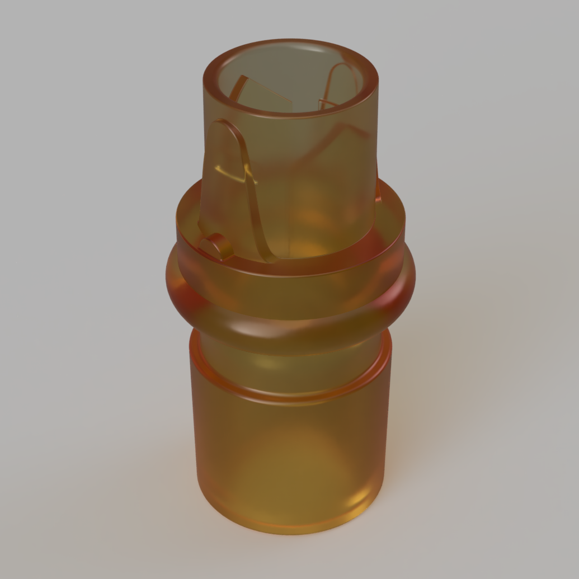
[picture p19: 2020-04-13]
Meta/Schematics and Renders/22M-Optiflow-adapter/22M-Optiflow-standing-2.png

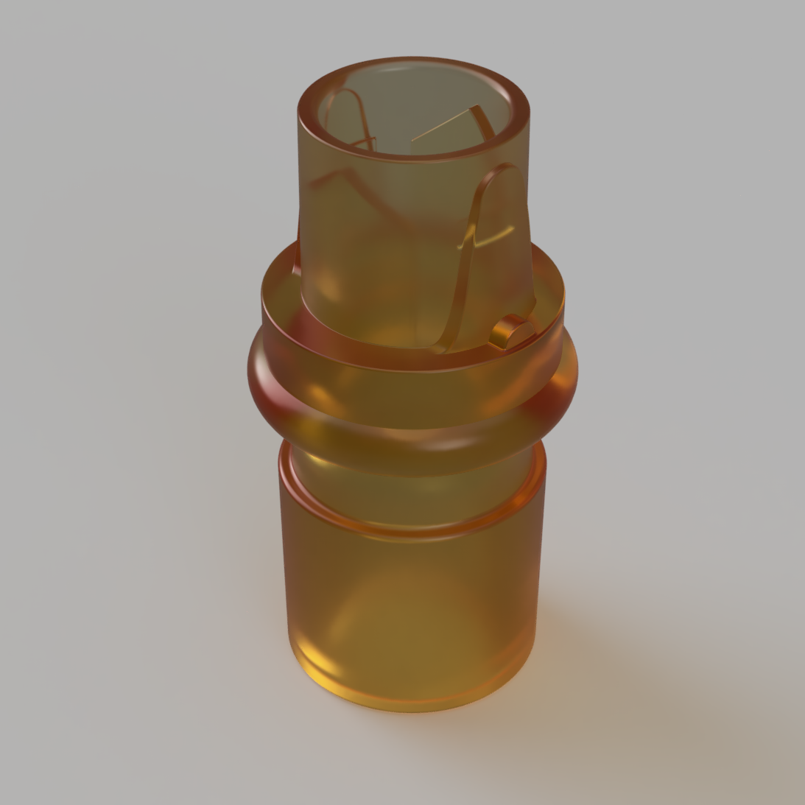
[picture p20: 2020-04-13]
Meta/Schematics and Renders/22M-Optiflow-adapter/22M-Optiflow-standing-1.png

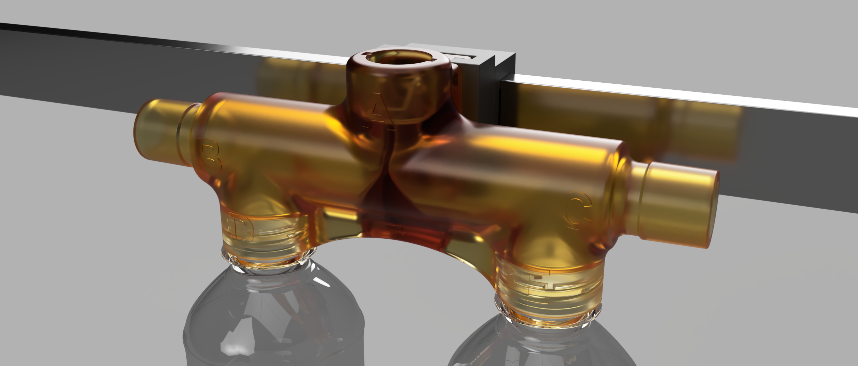
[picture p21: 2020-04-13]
Meta/Schematics and Renders/T-Coupling-V4/V4-on-rail-3.png

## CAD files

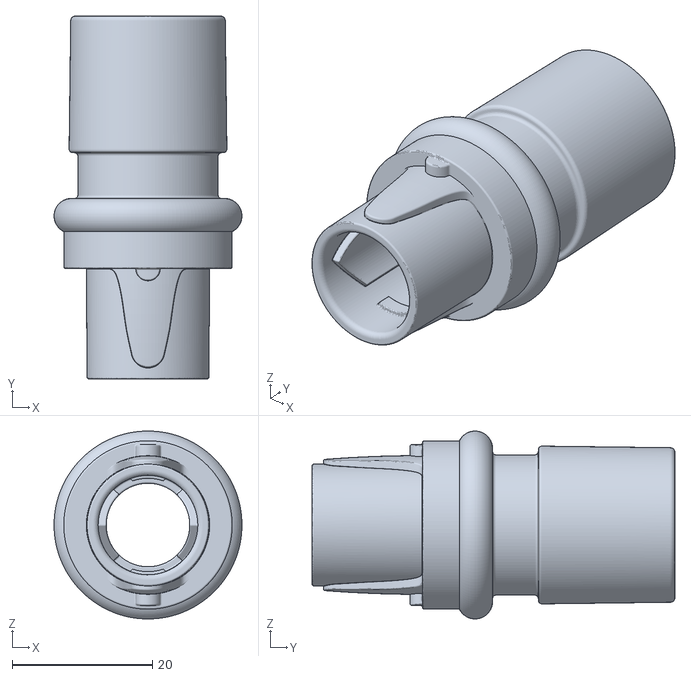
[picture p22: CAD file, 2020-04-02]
Models/Main/Adapter-Optiflow-22mm.stl
26.8 x 51.8 x 26.8

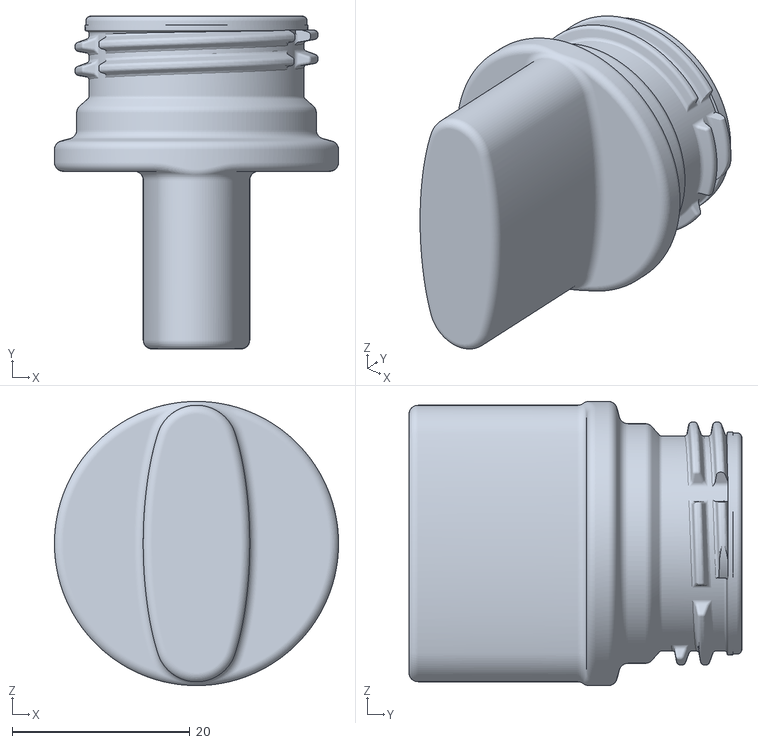
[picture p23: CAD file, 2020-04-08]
Models/Main/Optional/Plug-PET.stl
32.0 x 37.5 x 32.0

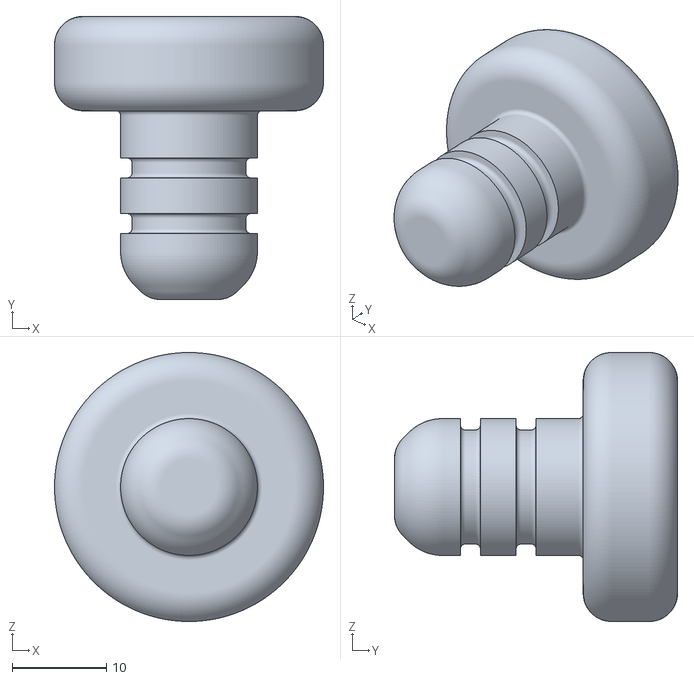
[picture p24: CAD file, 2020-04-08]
Models/Main/Optional/Plug-22mm-inside.stl
28.5 x 30.0 x 28.5

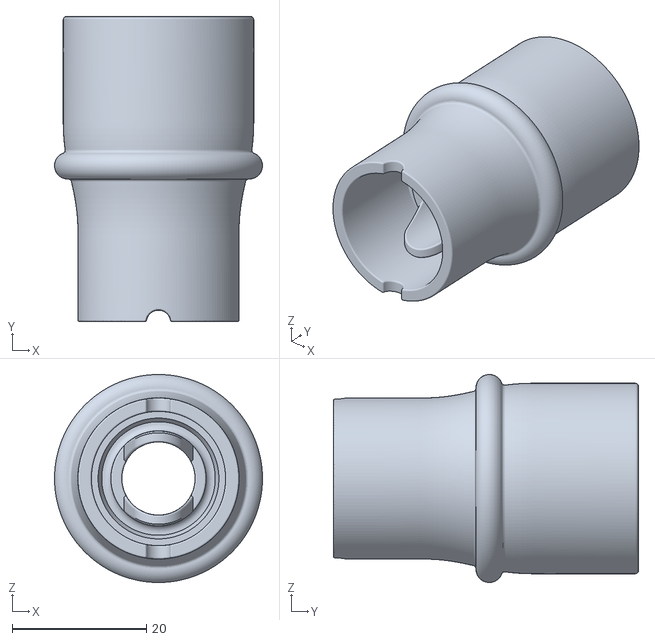
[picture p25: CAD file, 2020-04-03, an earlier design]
Models/Alt/Adapter-AirSpiral-22mm-F.stl
31.0 x 45.5 x 31.0

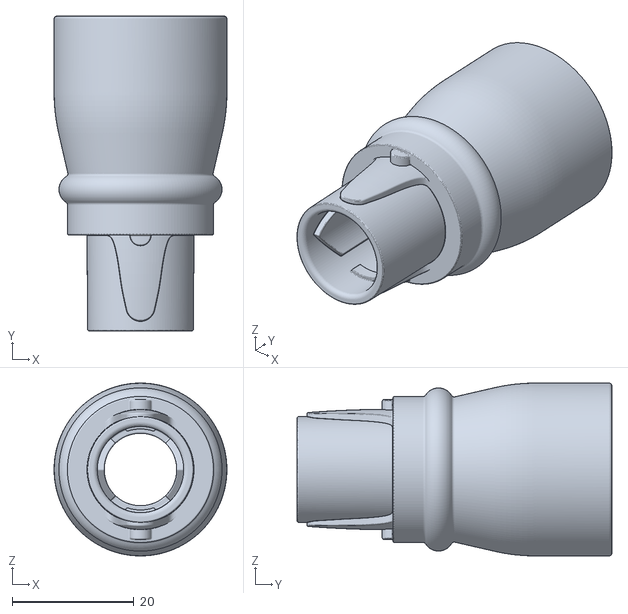
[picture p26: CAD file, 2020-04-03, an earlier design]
Models/Alt/Adapter-Optiflow-22mm-F.stl
28.4 x 51.8 x 28.4

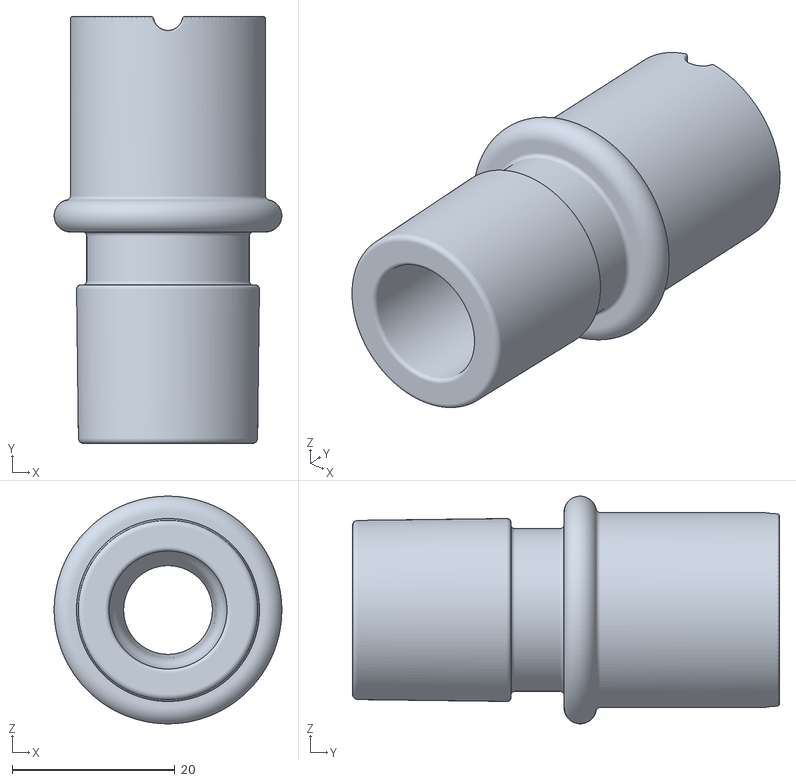
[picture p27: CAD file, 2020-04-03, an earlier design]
Models/Alt/Adapter-AirSpiral-22mm-M.stl
28.0 x 52.5 x 28.0

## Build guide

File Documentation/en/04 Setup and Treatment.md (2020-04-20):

# Setup

### Equipment needed

**a)** Fisher & Paykel Airvo 2.<br>
**b)** Pole stand with Airvo 2 and oxygen aggregate.<br>
**c)** 1 x Water Chamber\*. (900PT561)<br>
**d)** 1 x Fisher & Paykel AirSpiral\*. (900PT561)<br>
**e)** 2 x Nasal Cannula Fisher & Paykel Optiflow (OPT942 / OPT944 / OPT946)<br>
&nbsp;&nbsp;&nbsp;&nbsp;**i)** N.B! Both cannulae should be identic in size!<br>
**f)** 2 x CPAP / BiPAP-tubing<br>
&nbsp;&nbsp;&nbsp;&nbsp;**i)** 22 mm diameter and 1,8 m (3ft) length<br>
&nbsp;&nbsp;&nbsp;&nbsp;**ii)** E.g. Philips Respironics BiPAP / CPAP Reusable Flexible Tubing<br>
&nbsp;&nbsp;&nbsp;&nbsp;**iii)** N.B! Both tubes should be identic!<br>
**g)** _Optional_, subject to availability: 2 x Philips Tubing Isolator – colloquially ”Tube Sock”)<br>
&nbsp;&nbsp;&nbsp;&nbsp;**i)** Will help reduce condensation but not strictly needed for setup<br>
**h)** T-shaped connector, with markings ABCDE – ”T-Connector"<br>
**i)** 2 x Smaller 22mm to Optiflow adapter – ”Adapter”<br>
**j)** 2 x Cleaned 50 cl PET bottle – ”Collection bottle"<br>
**k)** 2 x Cable Tie (at least 100 mm in length)<br>
**l)** _Optional_: standard 22mm female plug or printable male plug<br>
&nbsp;&nbsp;&nbsp;&nbsp;**i)** Only used when starting HFNO with SHFNO prepared setup<br>
**m)** _Optional_: printable PET plug<br>
&nbsp;&nbsp;&nbsp;&nbsp;**i)** Only used when starting HFNO with SHFNO prepared setup<br>
**n)** Sterile water, 1000 ml.<br>

_\*N.B. That the Air Spiral tube generally comes in a set with a water chamber ("Tube & Chamber Kit"), only one of which is used in the SHFNO setup._

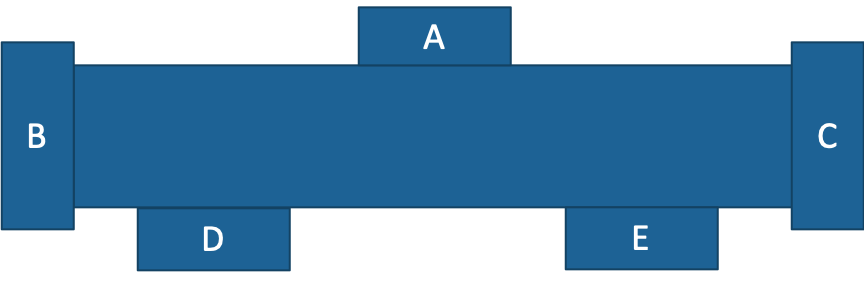
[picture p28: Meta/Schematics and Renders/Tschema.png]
Schematic T-Shaped Connector

Fig 1. Schematic illustration of T-Connector

### Setup

**1)** Attach (screw into place) two empty collection bottles to the ports on bottom of the T-connector, labeled D and E (will only fit these ports).<br>
**2)** Attach the concave back of the T-Connector to the pole stand, slightly above and contralaterally to the Airvo 2. The T-Connector should be mounted below patient height. The T-connector should be oriented so that the collection bottles point downward and the AirSpiral tube connects to the top of the T-connector. Secure the T-connector to the pole using two cable ties which can be treaded through the holes on the back of the T-connector.<br>
**3)** Prepare the water chamber by removing the blue port caps and fitting the supplied adapter. Fit the water chamber to the Airvo 2, ensure that the chamber clicks into place.<br>
**4)** Connect the sterile water bag to the water chamber.<br>
**5)** Connect the AirSpiral tube to the Airvo 2 and lock it into place by pushing down on sleeve.<br>
**6)** Attach the distal end of the AirSpiral tube to the port on the top of the T-Connector, labeled "A" (will only fit this port). If possible, loop over the top of the pole stand so that condensation is allowed to drain either to the Airvo 2 or the collection bottles.<br>
**7)** Connect the BiPAP/CPAP tubing to the two remaining ports on the T-connector (labeled B and C)†.<br>
**8)** (If "Tube Socks" are available, attach these to each of the tubings)<br>
**9)** Attach Adapter to the distal end of each BiPAP/CPAP tube.<br>
**10)** Attach Optiflow nasal cannula to each adapter.<br>
**11)** Attach oxygen aggregate to oxygen outlet.<br>
**12)** The setup is now ready to initiate treatment!<br>

†When starting HFNO with an SHFNO prepared setup, one side (B or C) of the T-connector is plugged. N.B. that both collection bottles are still needed.

|                                                                 Schematic view                                                                  |                                                        Prototype                                                        |
| :---------------------------------------------------------------------------------------------------------------------------------------------: | :---------------------------------------------------------------------------------------------------------------------: |
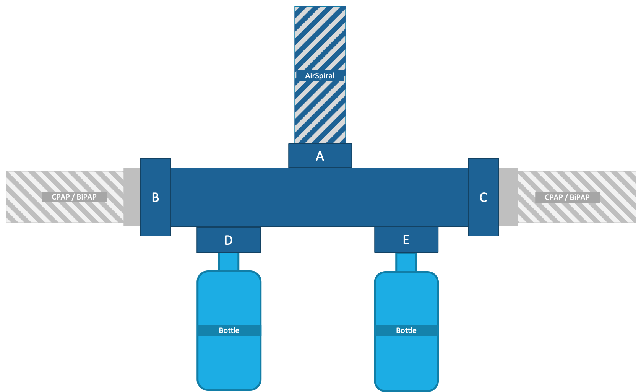
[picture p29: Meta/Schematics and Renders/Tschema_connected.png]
Schematic Connected T-Shaped Connector
|  | Photo of Connected T-Shaped Connector |

---

## Video instructions

(https://www.youtube.com/watch?v=IGeHuBSa3UQ)

---

# Initiation of Treatment

_N.B. These are provided as suggestions and should be adapted to local guidelines before SHFNO is put to use._

### Starting SHFNO

- Airflow is started at 60 litres/minute in the Airvo 2 system which delivers 30 litres/minute to each patient.
- FiO2 is started at 50% in the Airvo 2 system which delivers 50 % to each patient.
  - N.B. FiO2 is titrated as usual, FiO2 will be consistent between both patients and the Airvo 2 display
- Set temperature to 37 °C. If needed the temperature can be lowered to 34 °C.
- Titrate FiO2 to keep both patients within desired saturation range.

---

### Starting HFNO with an SHFNO prepared setup

- Setup according to steps above until you reach T-connector.
- Connect standard airway plug to empty side (at port labeled B or C) of T-connector
- Connect the rest of the T-connector as described above.
- Airflow is started at 30 litres/minute in the Airvo 2 system.
- FiO2 is started at 50% in the Airvo 2 system.
- Set temperature to 37 °C. If needed the temperature can be lowered to 34 °C.
- Titrate FiO2 to keep patient within desired saturation range.

---

### Transitioning from HFNO with prepared setup to SHFNO

_N.B. Water chamber and AirSpiral tube does not need to be changed if the setup has been prepared for SHFNO when adding a second patient to the setup._

- Connect CPAP/BiPAP to Adapter
- Connect Optiflow cannula to adapter (ensuring that it's of the same size as the other cannula in use).
- Attach nasal cannula to patient.
- Remove airway plug from T-connector and attach the prepared CPAP/BiPAP tube.
- Increase the airflow to 60 litres/minute.
- Titrate O2 to desired level.

---

### Transitioning from HFNO to SHFNO

_In order to decrease down time and ensure hygienic routines are being maintained, whenever possible transition from HFNO to SHFNO should be carried out by switching Airvo 2 systems. N.B. when transitioning a patient their Optiflow Nasal Cannula is kept, however water chamber and AirSpiral tube cannot be reused._

- Connect according to instructions above until having connected adapters to the distal end of the CPAP / BiPAP tube.
- If either of the patients is starting their treatment with SHFNO, rather than transitioning from HFNO, finish their setup according to the instructions above.
- Transition the Optiflow nasal cannula(e) already in use to the SHFNO-setup.
- Follow instructions "Starting SHFNO" and titrate desired treatment levels

---

### Transitioning from SHFNO to HFNO

- Check for condensation throughout the tube system and make sure that any accumulation of fluid flows back to the collection bottles.
- Stop Airvo 2 flow as well as oxygen supply.
- Remove CPAP / BiPAP tube from T-connector and attach standard plug.
- Change collection bottle for the affected side of the setup
  - _N.B. The inactive side needs either a collection bottle or a PET plug (model available as optional part of main set)._
- Start HFNO according to instruction "Starting HFNO with an SHFNO prepared setup"

---

## Condensation

Be observant to any condensation within the tube system. In SHFNO the condensation increases and water can accumulate within the CPAP/BiPAP tube.
Two times per shift, or around every 4 hours, the CPAP/BiPAP tube should be checked and raised in a matter ensuring that any fluid collection is helped to flow back to the collection bottle.

The collection bottle should be emptied before filling completely. It does not need cleaning when continuing treatment on the same patient after emptying. Make sure to reduce downtime by either removing the bottle and emptying it into another container and promptly screwing the bottle back on. If no other container is available, the bottle should be removed and another one attached to the system before disposing of the fluid collection. _N.B. The system needs both bottles attached in order to function properly_.

If possible, try to orient the CPAP and BiPAP tubes in a way that condensation can continuously flow back to the collection bottle. If a screen is used to divide patients, note that the tube cannot be passed over the screen as this affects flow of condensation.

---

## Sterile water

SHFNO consumes more water per litre of flow through the system due to condensation being accumulated in collection bottles rather than flowing back to the water chamber. The Airvo 2 will alert when the water chamber is dry, please ensure that you change the sterile water bag before the water chamber is completely empty.

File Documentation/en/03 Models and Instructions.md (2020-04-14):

# Models

These designs have all been made from scratch for this project. They use no prioprietary or 3D-scanned information. They are based on ISO standards when applicable - ISO-5356 for connectors and ISO-19054:2006 for mounts. All CAD work has been performed by Erik Cederberg at 3Dverkstan on behalf of the project.

---

### T-Connector

This connector splits air flow evenly and connects the proprietary connector of the distal end of the AirSpiral tube to the proximal end of two CPAP / BiPAP standard tubes.

It also features two drainage points to collect condensation. Two PET bottles are connected here to collect the fluid build up, and between the drainage point there is a splash guard. These features keep condensation from each patient separate. Thus the risk of cross contamination is kept to a minimum.

The design features clear markings so that the setup can be as easy and reliable as possible (also, each connector can only fit in the correct place).

|                                                 CAD view - Front                                                 | CAD view - Cross section                                                                                              |
| :--------------------------------------------------------------------------------------------------------------: | --------------------------------------------------------------------------------------------------------------------- |
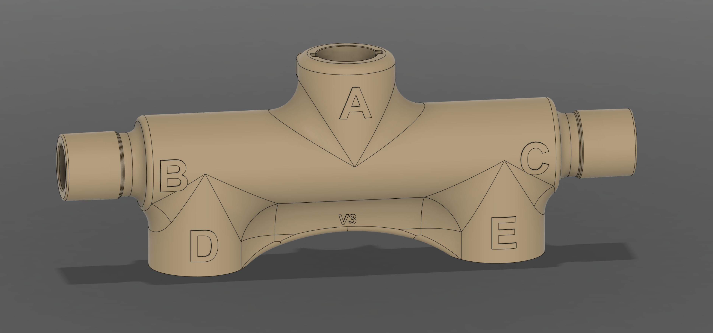
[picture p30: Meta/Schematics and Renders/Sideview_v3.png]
T-Shaped Connector Shell CAD view T-Shaped Connector
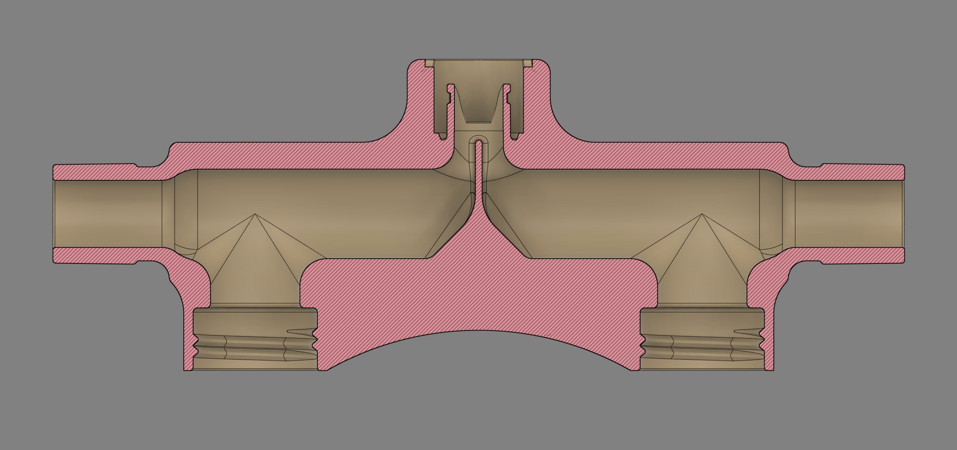
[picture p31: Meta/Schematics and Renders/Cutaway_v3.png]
T-Shaped Connector Cross Section Cross Section T-connector
|  |  |

The T-connector provided has a unified mount conforming the ISO-19054:2006 rail mount standard as well as enabling fastening with cable ties. The previous ziptie-only mount for the Airvo pole is therefore considered deprecated.

|                                                ISO-19054:2006 / Zip tie unified mount (male)                                                 |
| :------------------------------------------------------------------------------------------------------------------------------------------: |
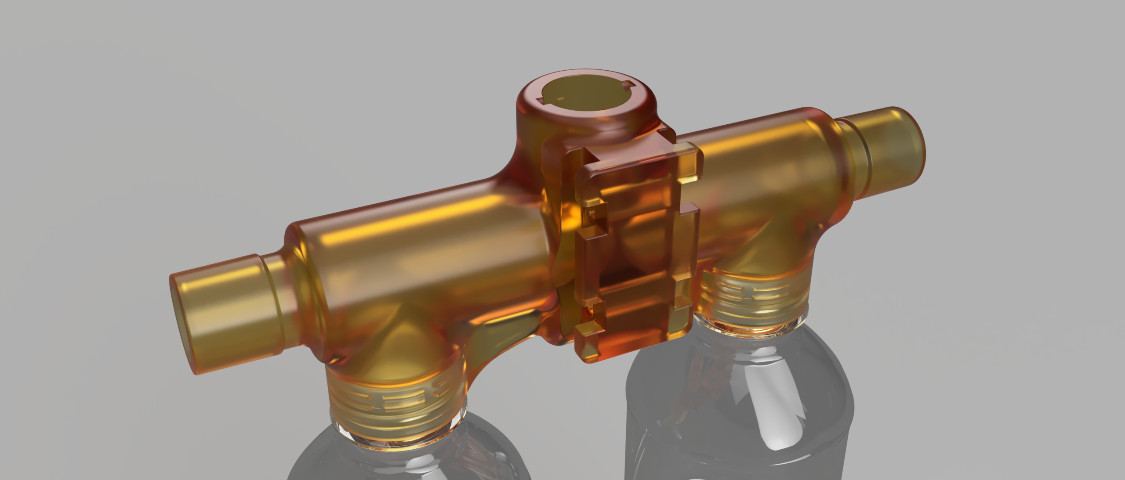
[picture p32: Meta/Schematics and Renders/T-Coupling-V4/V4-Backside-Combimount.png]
T-Connector back ISO-mount T-Connector back Combi-mount
|  |

---

### Adapters

We provide adapters for both the distal end of the AirSpiral tube and the proximal end of the Optiflow Nasal Cannula in two sizes / configurations, a male and female version.

For the core set you need two copies of the male Airvo connector with a male 22mm connector ("Airvo-M-22-M.stl")

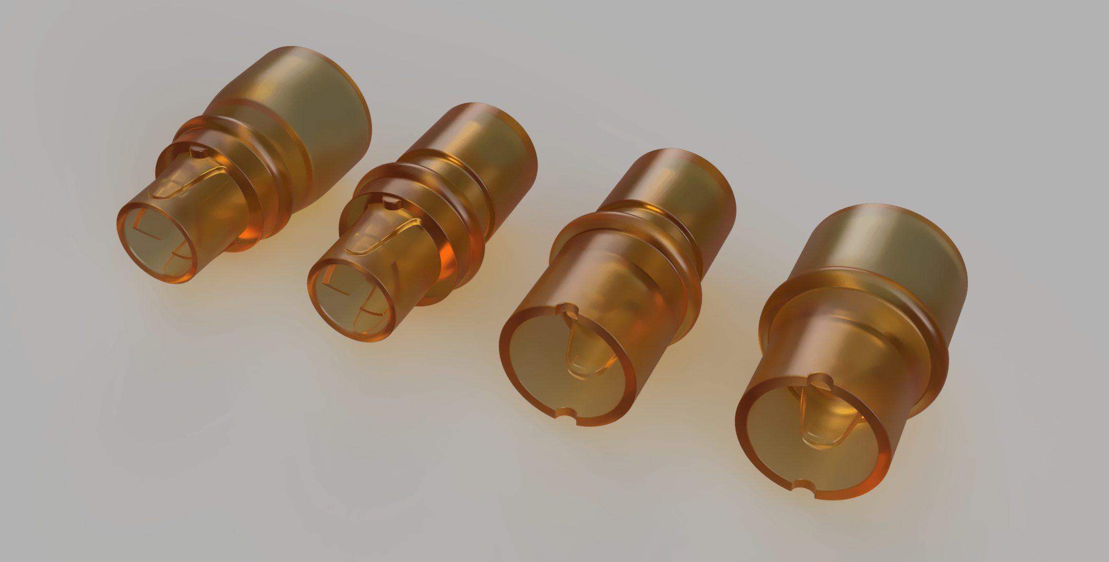
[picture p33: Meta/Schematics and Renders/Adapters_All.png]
All adapters


---

## Demo

This AR demo, only available on iOS, shows the 3D printed parts (for a standard setup) in actual size in Augmented Reality. Launch the demo by opening the link using an iPhone or iPad.

## [Launch AR-Demo](https://github.com/hessius/HFNOsplitter/blob/master/Meta/Other/Complete%20Set%20-%20Orientation.usdz?raw=true)

---

## Manufacturing Instructions

These prints are made to be printed using readily available resin 3D-printing methods. We recommend using SLA methods, specifically these instructions are based on the Formlabs Form 2/3 printers.

We recommend against using FDM/FFM printing as the high humidity and temperature is very suitable for bacterial growth and as FDM produces porous prints which cannot easily be sterilised.

All prints intended for medical use within this project are printed using the Formlabs Surgical Guide or Formlabs Dental SG Resin. These resins are approved for dental use and made to be autoclaved. When using one of these resins our risk assessment has been that the associated risks with the printing material are negligible.

[Formlabs Surgical Guide Datasheet](https://dental-media.formlabs.com/datasheets/SugicalGuideTechnicalDataSheet-101.pdf)

[Formlabs Surgical Guide Instructions for use](https://dental-media.formlabs.com/filer_public/56/69/566945b9-11c8-417a-a3e2-e88ec38668f5/surgicalguideifu.pdf)

[Formlabs Dental SG Datasheet](https://formlabs-media.formlabs.com/datasheets/DentalSG-DataSheet.pdf)

[Formlabs Dental SG Instructions for use](https://media.formlabs.com/m/1a0daf305c310d9d/original/-ENUS-Dental-SG-Instructions-for-Use.pdf)

If you attempt to print this on your own, we recommend that you have experience with these types of materials or are able to use the assistance of someone with that type of experience.

After validation is complete, we will provide complete printing instructions in the form of .form projects that others are free to use with the Formlabs standard software.

For all parts, we recommend that you turn off internal supports. For the T-connector, we recommend that you rotate the model so that one end of the long axis (so one of the 22mm connectors) is aiming toward the build plate in a ~50 degree angle, with around 10 degrees of tilt backwards.

For the adapters and plugs, we recommend that you raise them slightly off the print bed. For the adapters, orient the models with the 22mm/15mm coupling facing the build plate straight on. For the plugs, orient the models with th handle facing the build plate straight on. This way, support can be avoided on all critical surfaces, ensuring the best possible tolerance level.

| Complete set on build plate                                                                                                                  | Adapter straight up with support                                                                                                       | T-coupling angled with support                                                                                           |
| -------------------------------------------------------------------------------------------------------------------------------------------- | -------------------------------------------------------------------------------------------------------------------------------------- | ------------------------------------------------------------------------------------------------------------------------ |
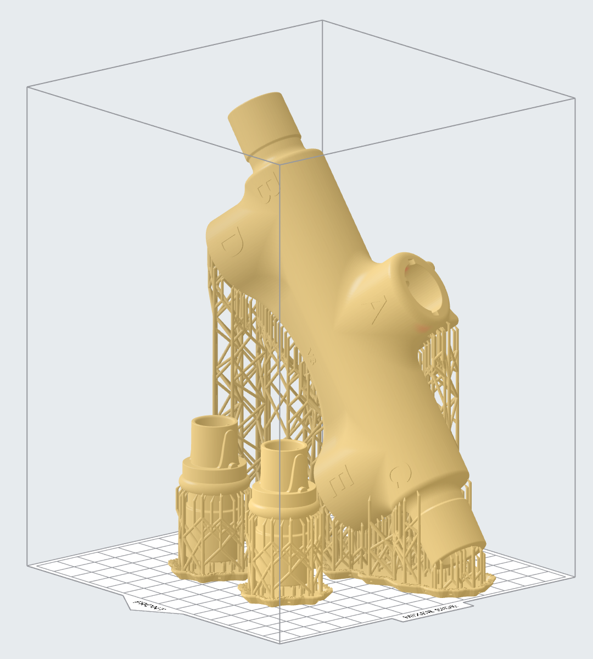
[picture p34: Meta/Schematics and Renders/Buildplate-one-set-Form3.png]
One complete set on a build plate
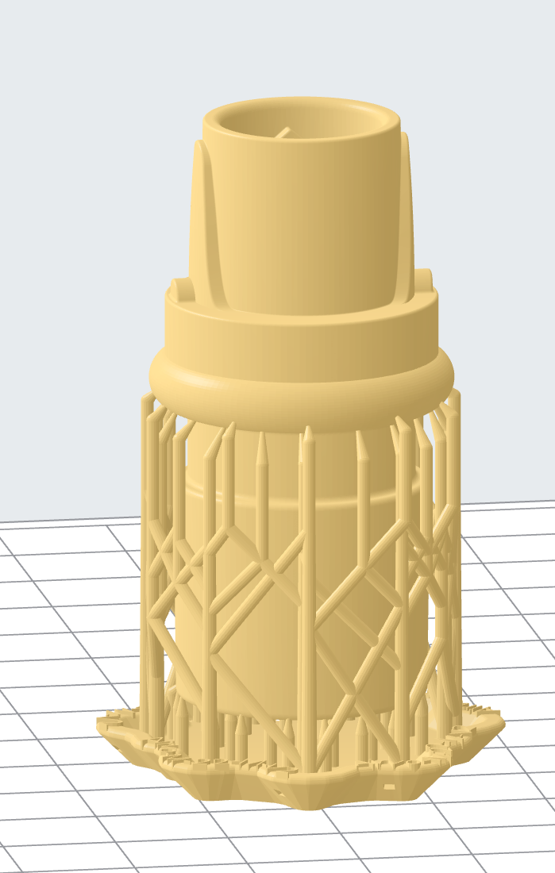
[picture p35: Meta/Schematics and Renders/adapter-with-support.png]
Adapter straight up with support
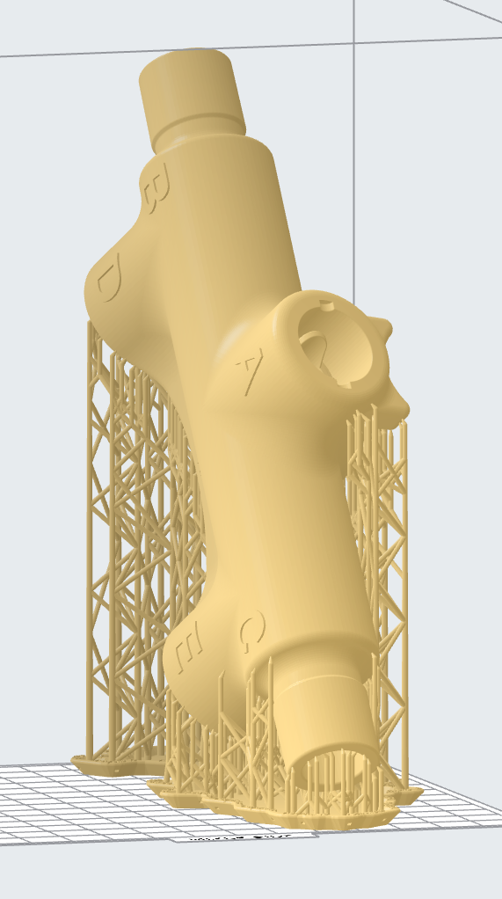
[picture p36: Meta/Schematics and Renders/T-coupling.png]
T-Coupling angled with support
|  |  |  |

### Changelog

| **Date**   | **Changes**                                                           |
| ---------- | --------------------------------------------------------------------- |
| 2020-04-05 | - Change B and C ports to 22mm male                                   |
| 2020-04-08 | - Rename STL-files (M/F -> Optiflow/AirSpiral)                        |
|            | - Add plugs to set.                                                   |
|            | - Add slight modifications to B, C, D, and E to better fit with plugs |
| 2020-04-10 | - Version bump: V4                                                    |
|            | - Add new ISO-19054:2006 compatible mounting slot                     |
| 2020-04-13 | - Add new "combimount" compatible with ISO-19054:2006 and zip ties    |  |

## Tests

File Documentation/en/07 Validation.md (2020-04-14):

# Validation

Basic validation has now been finished. This has consisted of multiple flow simulations of both air and water flows, as well as practical setup.

### Practical testing

Printed models, printed on different printers at different printing sites, have been tested with a wide variety of adapters and tubes conforming to either ISO standards or the proprietary Airvo connectors. With air leakage testing performed by submerging connections in water and running at full speed, no leakage could be identified.

---

### Air flow

Air flow simulations show that no clinically relevant resistance is added to the system by the SHFNO setup. Air flow is split evenly, and the collection bottles are to be considered dead space.
Condensation can however affect air flow, see below:

| Air flow                                                                                                                                                                | Air flow with condensation                                                                                                                                                  |
| ----------------------------------------------------------------------------------------------------------------------------------------------------------------------- | --------------------------------------------------------------------------------------------------------------------------------------------------------------------------- |
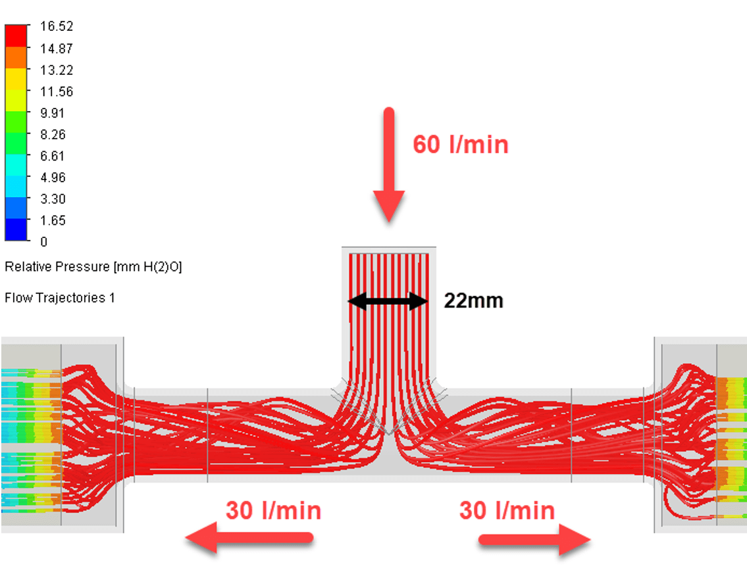
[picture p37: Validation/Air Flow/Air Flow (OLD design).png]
Air flow Air flow simulation
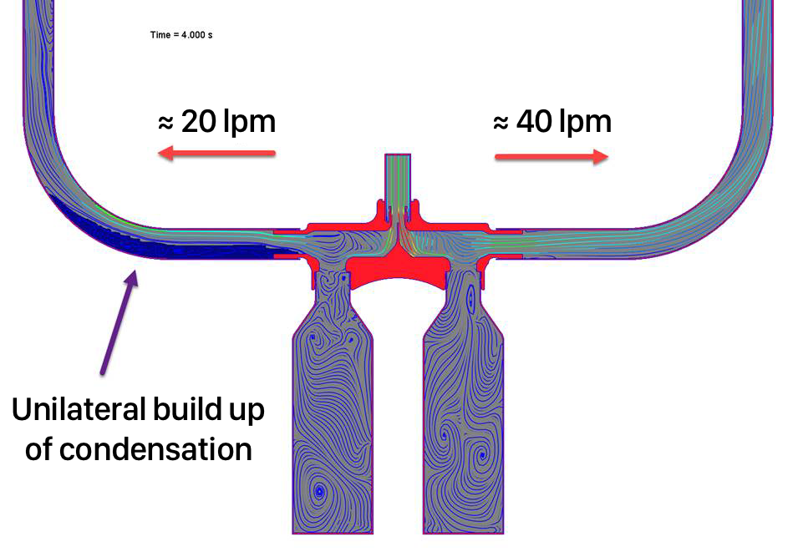
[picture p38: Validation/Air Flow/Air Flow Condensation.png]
Air flow + condensation simulation
|                                                                       |                                        |
| This simulation uses an older version of the design with a higher introduced resistance, even with an artificially high resistance the clinical effect is non-existent. | This simulation shows that with the extra unilateral condensation the resistance in one side of the setup is increased causing an uneven airflow that stabilises over time. |

---

### Condensation

While several steps have been taken to address condensation, it is notable that high levels of condensation can affect air flow (see simulation above).

**Slosh Simulations**
|Slosh at 0 lpm| Slosh at 60 lpm|
|---|---|
|[**View simulation video**](https://github.com/hessius/HFNOsplitter/blob/master/Validation/Slosh/1x%20slosh%200lps-1.mp4?raw=true)|[**View Simulation Video**](https://github.com/hessius/HFNOsplitter/blob/master/Validation/Slosh/2x%20slosh%2060lps-1.mp4?raw=true)
|When removing excess build-up of condensation toward the collection bottles at 0 litres/min our simulations show that a tiny amount of fluid is able to pass the separator between the bottles. This is only possible at 0 lpm, with large amounts of fluid and if fluid is returned at high speed.|During use at full flow, excess condensation might not be able to flow freely back to the collection bottles. This is normal and expected at high flows. If excess fluid cannot easily be returned it is recommended to temporarily reduce flow.

---

### Continued validation

While basic validation has been sufficient to bring this into use as a standby solution at the hospital of origin we are performing continued validation focused on measuring the air flow within the circuit. We are now close to a functioning setup with results expected mid-April. When results are available, this document will be updated accordingly.

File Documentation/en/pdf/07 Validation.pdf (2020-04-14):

07 Validation.md - SHFNO.org | Updated on: 4/14/2020

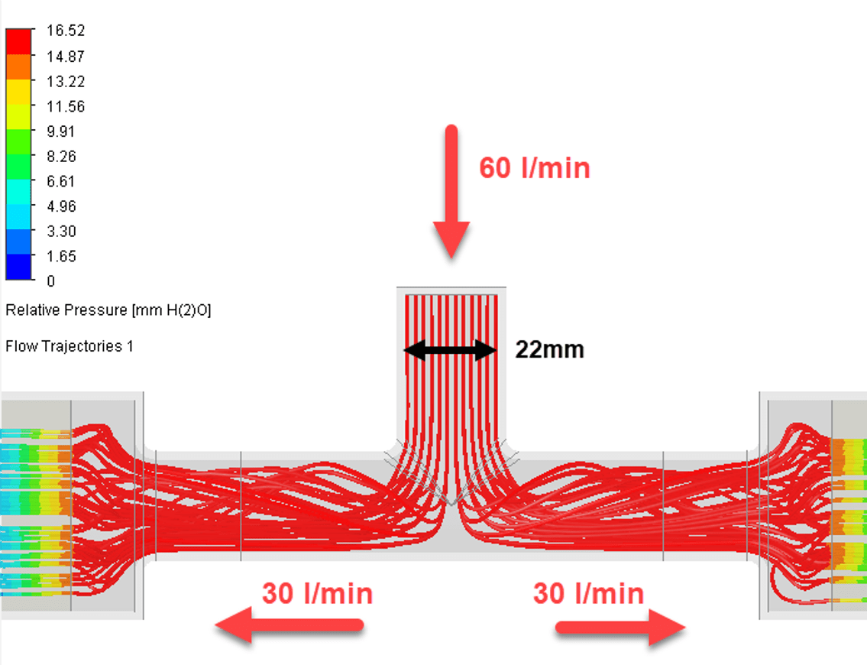
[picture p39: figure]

1 / 2

# Validation

Basic validation has now been finished. This has consisted of multiple flow simulations of both air and water flows, as well as practical setup.

Practicaltesting

Printed models, printed on different printers at different printing sites, have been tested with a wide variety of adapters and tubes conforming to eitherISO standards orthe proprietary Airvo connectors. With airleakage testing performed by submerging connections in water and running at full speed, no leakage could be identified.

Airflow

Airflow simulations show that no clinically relevantresistance is added to the system by the SHFNO setup. Air flow is split evenly, and the collection bottles are to be considered dead space. Condensation can however affect airflow, see below:

Air flow | Air flow with condensation

This simulation uses an older version of the design with a higherintroduced resistance, even with an artificially high resistance the clinical effect is non-existent.

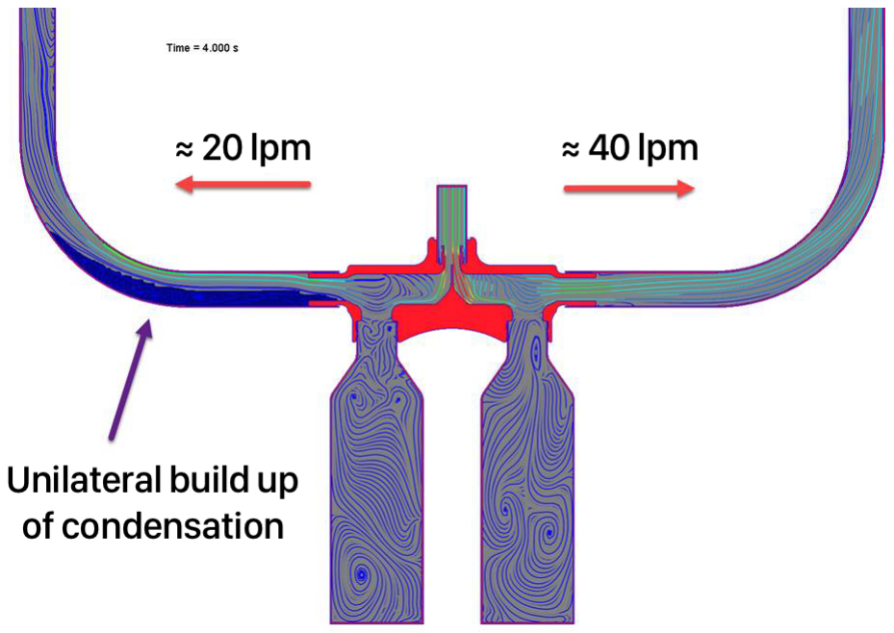
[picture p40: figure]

This simulation shows that with the extra unilateral condensation the resistance in one side of the setup is increased causing an uneven airflow that stabilises overtime.

Condensation

While several steps have been taken to address condensation, it is notable that high levels of condensation can affect airflow (see simulation above).

SloshSimulations

Slosh at 0 lpm | Slosh at 60 lpm

07 Validation.md - SHFNO.org | Updated on: 4/14/2020

2 / 2

Slosh at 0 lpm | Slosh at 60 lpm
View simulation video (https://github.com/hessius/HFNOsplitter/blob/master/Validation/Slosh/1x%20slosh%200lps-1.mp4?raw=true) | View Simulation Video (https://github.com/hessius/HFNOsplitter/blob/master/Validation/Slosh/2x%20slosh%2060lps-1.mp4?raw=true)
When removing excess build-up of condensation toward the collection bottles at 0 litres/min our simulations show that a tiny amount of fluid is able to pass the separator between the bottles. This is only possible at 0 lpm, with large amounts of fluid and if fluid is returned at high speed. | During use at full flow, excess condensation might not be able to flow freely back to the collection bottles. This is normal and expected at high flows. If excess fluid cannot easily be returned it is recommended to temporarily reduce flow.

Continued validation

While basic validation has been sufficient to bring this into use as a standby solution at the hospital of origin we are performing continued validation focused on measuring the airflow within the circuit. We are now close to a functioning setup with results expected mid-April. When results are available, this document will be updated accordingly.

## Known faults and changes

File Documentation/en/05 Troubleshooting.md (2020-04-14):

# Troubleshooting

These instructions are all designed to address a catastrophic situation. If forced to use the SFHNO protocol please take extra precautions. We recommend keeping a reservoir mask by the patient's side at any time when there is ongoing SHFNO.

If a patient were to suddenly deteriorate during ongoing SHFNO, the following checklist needs to be completed in addition to regular protocol. **The checklist should also be completed by the treating nurse at the beginning of every shift.**

### Checklist

For both sides of the setup:

1. **Check Nasal Cannula**

   Is the nasal cannula correctly situated in the nares? N.B. The Airvo system's built-in warning for obstructed flow does not work during SHFNO.

   Ensure that there's no build-up of condensation within the tube leading up to the nasal cannula.

1. **Check all connections**

   Start proximally and work your way distally. Ensure that all connections are securely fitted. If any connection seems loose, try changing adapter or T-connector.

1. **Check CPAP / BiPAP tube**

   Ensure that there are no sharp angles to the tube, restricting flow.

   Ensure that there is no build up of condensation within the tube.

1. **Check AirSpiral tube**

   Ensure that there are no sharp angles to the tube, restricting flow.

   Ensure that there is no build-up of condensation within the tube.

1. **Check collection bottles**

   Ensure that the bottle is securely connected, and that it is not completely filled with fluid.

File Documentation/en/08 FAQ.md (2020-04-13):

## FAQ

_This section will be updated continuously._

- ### What if our guidelines don't restrict flow at 30 litres/minute?

  You might still be able to increase your capacity for HFNO by utilising SHFNO when possible.

  A simple example: Let's say you have 20 HFNO systems, and 30 patients deemed to benefit from HFNO but only half of them are able to be treated with 30 lpm of air flow.

  Without SHFNO you (obviously) will only be able to treat 20 of those patients. With SHFNO you're now able to treat 25-27 patients instead of 20. Thus SHFNO can be part of a resource utilisation strategy in a crisis situation even though you might not be able to apply it across the board.

- ### What if a patient needs more than 30 lpm?

  Then they are not eligible for SHFNO with the Airvo 2 system.

- ### So, should we keep using this after COVID-19?

  No.

- ### Why don't we just buy more systems?

  Please do! If you are able to treat these patients with HFNO by any other means, please do not try this. This is meant as a last resort during a time of crisis.

- ### Why use PET bottles?

  They are ubiquitous, have a standardised connector, are cheap, and they are food safe.

- ### What are the risks associated with this?

  While we are not able to accept any liability for this modified setup, we have carried out a rigorous risk assessment according to ISO-14971:2012 and all identified risks have been addressed in design revisions, documentation and implementation strategy. We advise that you perform, at the very least, a simplified risk analysis.

  Further, one needs to acknowledge the very special circumstances where the risks associated with not being able to provide treatment might be catastrophic.

- ### What do the 3D printed parts cost?

  The cost of materials is around USD 40. Many print shops now waive the production costs for health care providers. Ask your local shop!

- ### How do I find a local 3D print shop?

  Many universities (and university hospitals) use the types of printers recommended for these types of applications. Also larger dental practices might carry these in your area. If you can find a local reseller of the resin you might be able to get information on where to ask for help.

- ### Can you sell me a kit?

  No. We recommend against selling kits as there are possible legal ramifications. However if you produce these for someone else you are allowed to charge for contract manufacturing i.e. materials used and print time reimbursement if applicable.

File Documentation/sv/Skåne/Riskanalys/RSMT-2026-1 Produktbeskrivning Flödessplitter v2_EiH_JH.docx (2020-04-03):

Produktbeskrivning

Flödessplitter för högflödesgrimma

Projektet omfattar följande inventarier:
Benämning: | Nummer/kod:
| 202001962, 202001973 och 202001976

Innehållsförteckning

# 1. Inledning

Denna produktbeskrivning är upprättad i enlighet med tillämpliga delar av standarden för Klinisk prövning av medicintekniska produkter – God klinisk praxis Annex B SS-EN ISO 14155:2011 (1).

## 1.1. Syfte och omfattning

Syftet med dokumentet är att beskriva hur de krav som definierats är implementerade samt hur produkten är uppbyggd.

# 2. Bakgrund

## 2.1. Resultat från förstudie och forskning

Då det uppstod ett akut bristläge i försörjning med material och apparater grund av Covid-19 har det tagits fram en lösning för att kunna dela på en Optiflow till två patienter inom sjukvården.

Ett flertal olika varianter och modeller har provats fram, i form av design och idéer, samt genom simuleringar.

## 2.2. Behov

Syftet med produkten är att kunna ge fler patienter möjlighet till behandling med högflöde än vad som finns i form av apparatur att tillgå. Genom att dela på flödet från en apparat till två patienter kan man teoretiskt dubblera möjligheten till behandling. Ytterligare delning av flödet till fler patienter är teoretiskt möjligt baserat på detta arbete genom vidareutveckling av T-kopplingen.

Denna produkt ger en möjlighet till att täcka ett akut behov som är omöjligt att tillfredsställa på marknaden.

# 3. Produktidentifikation

Produkten identifieras med inventarienummer i Medusa:

T-koppling: 202001962.

Optiflow-adapter: 202001973

Hela projektet: 202001976

Tillverkare:
Medicinsk Teknik Skåne, Digitalisering IT och MT,
291 89 Kristianstad

## 3.1. Märkning av produkt:

Märkning görs på förpackning med hjälp av etikett, detta då det inte är möjligt att sätta etikett på själva produkten: dels av praktiska skäl dels ur er ett hygienperspektiv.

Etikett 1: Egentillverkad produkt, fou.mt@skane.se

Etikett 2: Egentillverkning, inventarienummer

# 4. Målgrupp och användarmiljö

Personal inom Region Skånes hälso- och sjukvård som har behov av att kunna dela på en Optiflow till två patienter inom sjukvården.

# 5. Avsedd användning

I enlighet med tillverkaren för utrustningen Airvo 2 (Fisher & Paykel Healthcare).

T-kopplingen är endast avsedd att kopplas mellan AirSpiral™ Tube och C-PAP slang. På avsedda platser på T-kopplingen skall PET-flaska vara ansluten, detta för att kondensvatten skall avledas och systemet blir tätt.

## 5.1. Rengöringsmetod

Denna metod gäller för T-kopplingen och Optiflow-adaptern (2). Övriga komponenter hanteras i enlighet tillverkarens anvisningar.

- Disk enligt gängse praxis

Samt ett av nedanstående

- Autoklav enligt gängse praxis 134 grader, 4 minuter / 121 grader, 15 minuter
- Nedsänkning i ytdesinfektionsbas i minst 5 minuter

# 6. Kravställning

PK001: Produkten skall dela upp flödet i två grenar med ringa förluster

PK002: produkten skall var baserad på tillgängligt material på sjukhuset eller sådant som går att framställa och använda på ett lämpligt sätt.

RK001: Avstå delad behandling av bärare av MRB

RK002: Avstå delad behandling av patient med känd bakteriell sekundärinfektion(?)

RK003: Teknisk lösning i anslutning till T-koppling som avleder kondensvatten från respektive patient.

RK004: I kliniskt bruk endast användning av CE-märkt plast godkänd för oralt bruk (Formlabs Dental SG)

RK005: Delning endast mellan patienter med relativt lik kroppshydda

RK006: Delning endast mellan patienter med samma storlek på grimma

RK007: Kontroll av korrekt slang- och grimm-läge, särskilt vid upplevd försämring

RK008: Vid start av optiflow eftersträvas enskild behandling till dess att inställningar justerats

RK009: Övergång till delad behandling vid stabiliserade inställningar

RK010: Övergång till delad behandling till patient med samma inställningar

RK011: Utskrivna komponenterna görs i plast som tål Autoklav

RK012: Rengöring av apparat ska ske på veckobasis

RK013: Krav på täthet på konstruktionen

RK014: Mekanisk rengöring och avsyningen på varje exemplar innan första användning.

RK015: Kontroll av design av tillverkade komponenter

RK016: Processrutin för tillverkningen (utskriften)

# 7. Produkt

Produkten är egentillverkad inom Region Skåne enligt Socialstyrelsens föreskrifter (3) och den särskilda Covid-19 handledningen som IVO har publicerat () för den specifika verksamheten under Medicinsk Teknik Skånes ledningssystem (4) i enlighet med ISO 13485:2012, Medicintekniska produkter – Ledningssystem för kvalitet (5). Detta dokumenteras inte genom en försäkran om överensstämmelse (6) utan som en planerad avvikelse då den kompletta dokumentationen inte kan prioriteras i detta läge vilket är helt i linje med IVOs uttalande (7). Produkten är utvecklad i enlighet med produktutvecklingsprocessen (8). Riskhantering har skett i enlighet med ISO 14971:2012 (9).

## 7.1. Konstruktion

HFNO

O²

H²O

30 lpm

50% FiO2 (15 lpm)

Bild 1 Standardkoppling för en patient. HFNO - High Flow Nasal Oxygen.

Standardkoppling utgår från följande delar:

H²O

HFNO

O²

60 lpm

50% FiO2 (30 lpm)

30 lpm

50% FiO2 (15 lpm)

30 lpm

50% FiO2 (15 lpm)

Bild 2 Delad koppling

Konstruktionen består av en kombination av de vanliga delarna för Optiflow kompletterat med en t-koppling, CPAP-slangar för att uppnå en bra längd samt en adapter från C-PAP-slang till högflödesgrimman.

### 7.1.1. Syrgasaggregat

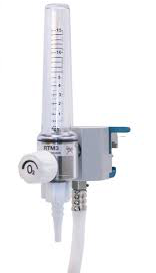
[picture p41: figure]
Produktkatalog

Bild 3 Syrgasaggregat

Standardkomponent. Finns med olika kapacitet. För att uppnå maximal effekt (100% FiO2 vid 60 lpm) krävs 0-60 l, enligt rådande behandlingsriktlinjer för COVID-19, för vilken lösningen är framtagen, krävs endast 0-30l (50% FiO2 vid 60lpm).

### 7.1.2. Airvo™ 2

De facto standard för HFNO i Sverige. Airvo 2 från Fisher & Paykel Healthcare, i folkmun ”Optiflow”. Levererar syresatt uppvärmd fuktad luft

- FiO2 21-100%
- Flöde 2-60 lpm

### 7.1.3. AirSpiral™ Tube

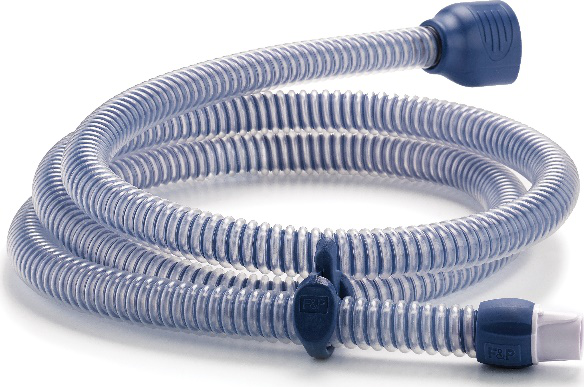
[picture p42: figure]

Bild 4 AirSpiral™ Tube

Standardkomponent. Uppvärmd luftslang (mot kondens).

Specifikationer:

  - Längd: 1.2 m
  - Diameter: 22 mm
  - Värms med kopparslinga
  - Proprietära kopplingar

### 7.1.4. T-koppling

En bild som visar inomhus, bord, flaska, sitter Automatiskt genererad beskrivning

Bild 5 T-koppling

Från: Distal AirSpiral

Till: Standardiserad koppling och vätskeuppsamlingsflaska

Utskriven med 3dprint i dental-material (10) i enlighet med rutin för utskrift (11).

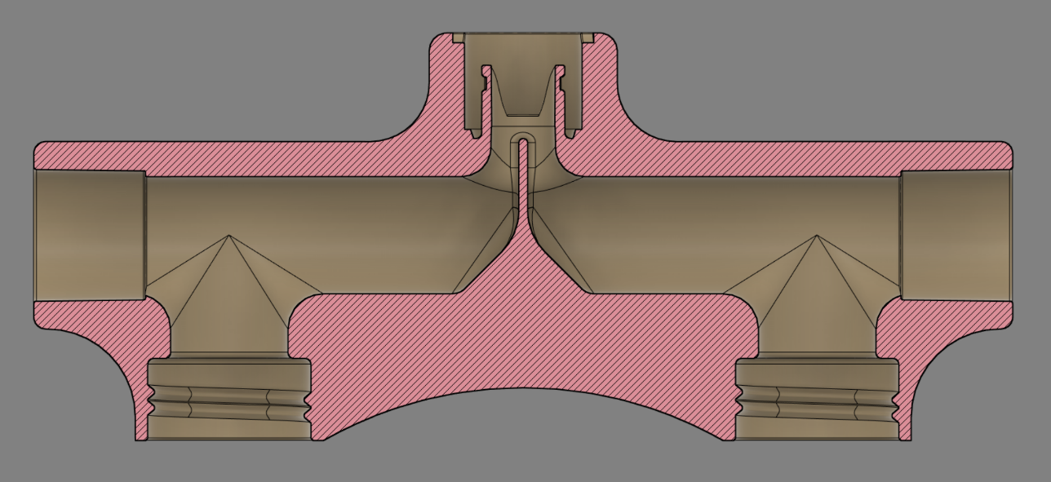
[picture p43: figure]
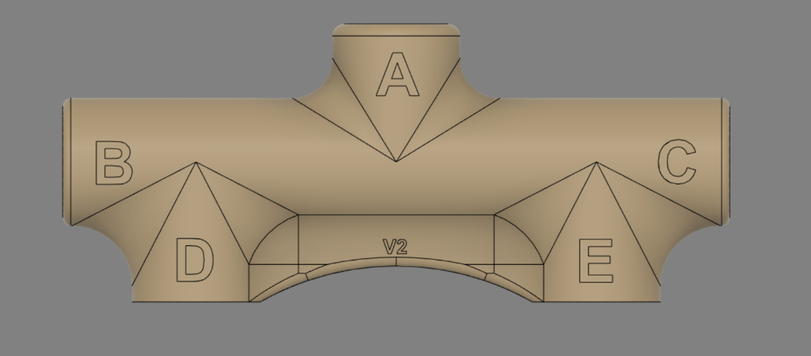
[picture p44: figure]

### 7.1.5. Philips Respironics BiPAP / CPAP Reusable Flexible Tubing.

Standard-CPAP-slang

Specifikationer:

- Längd: 1.8 m
- Diameter: 22 mm
- Standardiserad koppling

### 7.1.6. Philips CPAP-Slangisolator

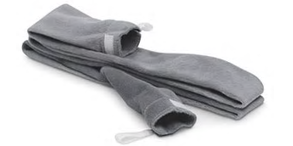
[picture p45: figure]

Bild 6 Philips C-PAP slangisolator

”Slangstrumpa” som ger en passiv isolering. Hjälper till att bibehålla temperatur och minska kondens men är ej strikt nödvändig (å andra sidan ej begränsande).

### 7.1.7. Optiflowadapter

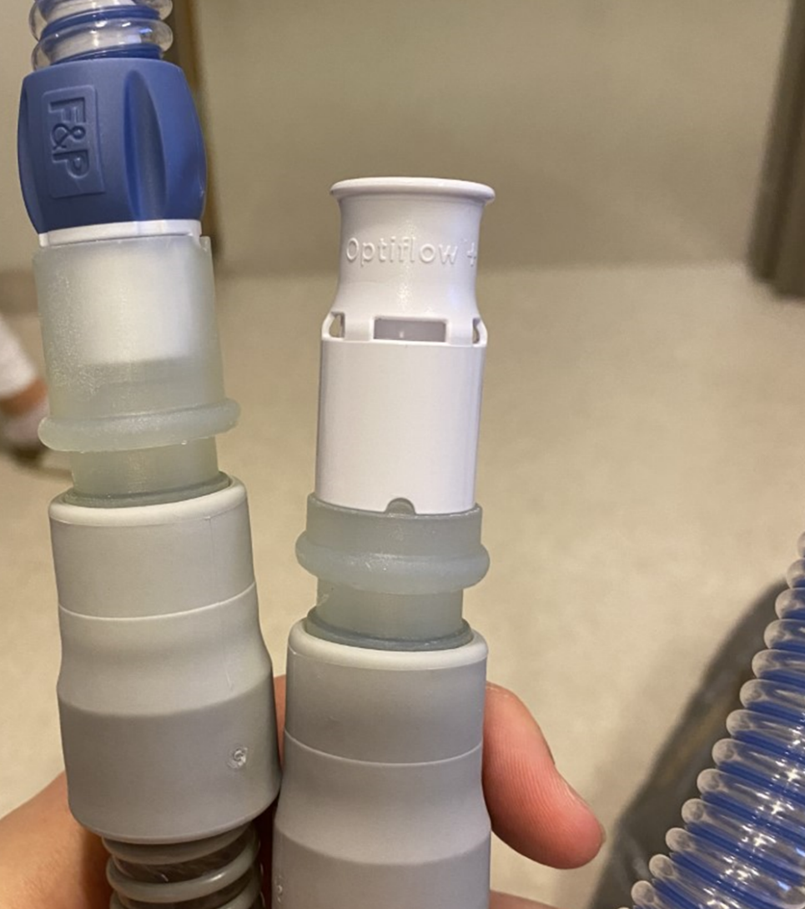
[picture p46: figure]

Bild 7 Optiflowadapter, denna bild visar en utskrift i vanlig plast

Från: Standardiserad koppling

Till: Proximal Optiflow

Utskriven med 3dprint i dental-material (10) i enlighet med rutin för utskrift (11).

### 7.1.8. Optiflow™ Nasal Cannula

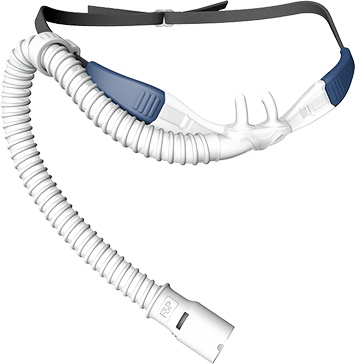
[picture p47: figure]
Optiflow™ Nasal Cannula for myAIRVO 2 – Tri-Med Medical Supplies, Inc.

Bild 8 Optiflow™ Nasal Cannula

Standardkomponent. Semipermeabel slang för att motverka kondens. I distala änden finns högflödesgrimma. Proprietär koppling (proximalt).

## 7.2. Mjukvara

Produkten innehåller ingen mjukvara.

## 7.3. Designhistorik

V0.1: första skräddarsydda T-kopplingen

V0.2: T-koppling med anslutning för PET-flaska för att avleda kondensvatten

V0.3: T-koppling med anslutning för PET-flaska och designad för att minska risk för korskontamination

# 8. Testning utförd innan kliniskt bruk

Flödessimulering, se Appendix A: Flödessimulering gjord med HME-Filter med specificerat motstånd 1.6 cm H2O vid 30 lpm. Bekräftar den teoretiska kapaciteten och visar jämnt distribuerat flöde mellan patienterna utan relevant motstånd skapat av filter eller ökad slanglängd. OBS att filter inte används i den färdiga lösningen

Framtagning och produktion: komponenter plockas från C-PAP vilket inte är en bristvara. De specialtillverkade delarna görs genom 3dprint på sjukhuset i Lund respektive 3Dverkstan i Stockholm.

Kraven har gåtts igenom, se Appendix B. Följande krav återstår att realisera:

- Rutin för tillverkning och kontroll innan första användningen
- Instruktion för användning inom Region Skåne
- Validering av rengörings- och steriliseringsmetod för dessa komponenter

# 9. Varningar

► Använd inte produkten om den är mekaniskt skadad

► Använd inte produkten eller den sterila förpackningen är skadad.

► Använd inte produkten efter dess utgångsdatum på den sterila förpackningen.

# 10. Servicemanual

Se rengörings- och steriliseringsmetod.

I övrigt skall produkten inte servas utan kasseras i sådant fall.

# 11. Existerande klinisk data

DentalSG är en CE-märkt plast för surgical guides främst inom käkkirurgi.

3dprint som teknik har använts i ett flertal lyckade projekt för egentillverkning inom SUS Lund: gelapplikatorn (2016), gjutform för kraniplastik (2019-), nålguide (2020) med flera.

Behandlingen med Optflow är en vedertagen metod med lång och beprövad erfarenhet.

# 12. Referenser

1. SS-EN ISO 14155:2011, Klinisk prövning av medicintekniska produkter – God klinisk praxis.

2. EXDO-191204, Application-Guide_Surgical-Guides_EN.

3. SOSF 2008:1, Användning av medicintekniska produkter i hälso- och sjukvården .

4. PROC-10013, Processbeskrivning Kvalitetsmanual.

5. ISO 13485:2012, Medicintekniska produkter – Ledningssystem för kvalitet – Krav för regulatoriska ändamål.

6. TMPL-10031, Försäkran om överensstämmelse.

7. https://www.ivo.se/publicerat-material/nyheter/2020/ivos-svar-pa-fraga-gallande-anvandning-och-hantering-av-ventilatorer-tillhandahallna-bl.a.-fran-socialstyrelsens-beredskapslager/. IVO_s svar på fråga gällande användning och hantering av ventilatorer. [Online]

8. PROC-10011, Processbeskrivning Produktutveckling.

9. ISO 14971:2012, Medicintekniska produkter – Tillämpning av ett system för riskhantering för medicintekniska produkter.

10. EXDO-191205, DentalSG-DataSheet.

12. TMPL-10029, instruktion med Checklista ledningens genomgång.

13. ISBN:978-91-86301-28-6, Riskanalys & Händelseanalys - handbok för patientsäkerhet.

14. IEC 62366, Medical devices - Application of usibility engineering to medical devices.

15. TMPL-10025, Produktbeskrivning, mall.

16. TMPL-10028, Teknisk fil, Mall.

17. TMPL-10022, Riskhanteringsplan Mall.

18. TMPL-10030, Riskhanteringsrapport, mall.

19. TMPL-10038, Riskanalysschema, mall.

20. TMPL-10043, Mötesanteckningar riskanalysmöte, mall.

21. PROC-10012, Processbeskrivning Tillverkning.

# 13. Revisionshistorik

Version | Datum | Versionsförändring av | kommentar
0.1 | 2020-03-31 | Per Nordqvist | Första version av dokumentet på nytt nummer
~~1.0~~ | | | ~~Godkänd version~~

# Appendix A Simuleringar

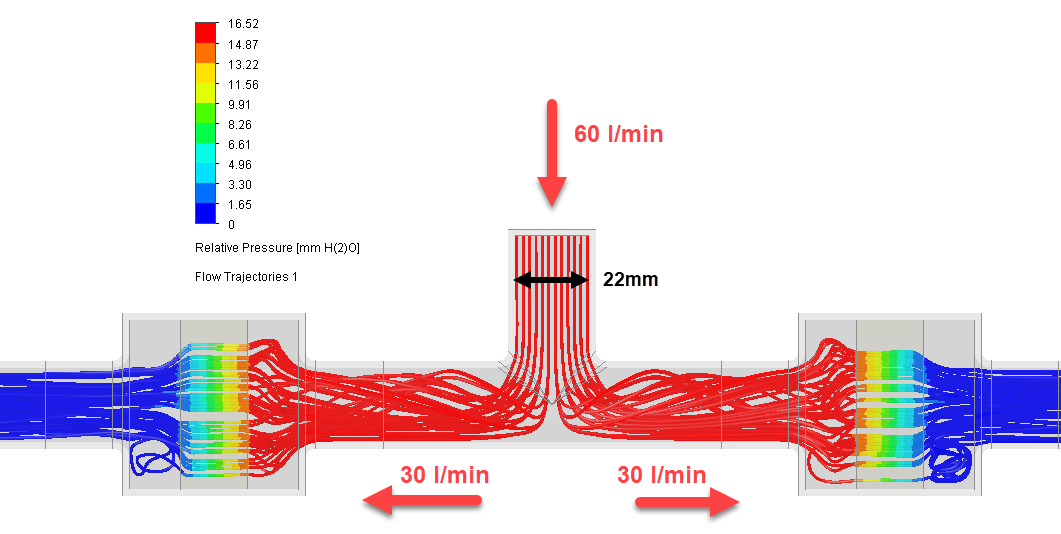
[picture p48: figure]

# Appendix B Kravgenomgång

PK001: Produkten skall dela upp flödet i två grenar med ringa förluster

PK002: produkten skall var baserad på tillgängligt material på sjukhuset eller sådant som går att framställa och använda på ett lämpligt sätt.

RK001: Avstå delad behandling av bärare av MRB

RK002: Avstå delad behandling av patient med känd bakteriell sekundärinfektion(?)

RK003: Teknisk lösning i anslutning till T-koppling som avleder kondensvatten från respektive patient.

RK004: I kliniskt bruk endast användning av CE-märkt plast godkänd för oralt bruk (Formlabs Dental SG)

RK005: Delning endast mellan patienter med relativt lik kroppshydda

RK006: Delning endast mellan patienter med samma storlek på grimma

RK007: Kontroll av korrekt slang- och grimm-läge, särskilt vid upplevd försämring

RK008: Vid start av optiflow eftersträvas enskild behandling till dess att inställningar justerats

RK009: Övergång till delad behandling vid stabiliserade inställningar

RK010: Övergång till delad behandling till patient med samma inställningar

RK011: utskrivna komponenterna görs i plast som tål Autoklav

RK012: rengöring av apparat ska ske på veckobasis

RK013: krav på täthet på konstruktionen

RK014: mekanisk rengöring och avsyningen på varje exemplar innan första användning.

RK015: Kontroll av design av tillverkade komponenter

RK016: processrutin för tillverkningen (utskriften)

\\RSFS083\Hem6$\181806\_Dokument\Egentillverkning\0_Covid-19\Flödessplitter\Teknisk fil\RSMT-2026-1 Produktbeskrivning Flödessplitter v2.docx [Ange MallID] Original lagras elektroniskt, observera att utskrivet dokument inte gäller som original. Sid Användaren ansvarar för att gällande revision anv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

Region Skåne Digitalisering IT och MT Medicinsk teknik Skåne Organisationsnummer 291 89 Kristianstad Lasarettsgatan 37, 221 85 Lund 232100-0255 Original lagras elektroniskt, observera att utskrivet dokument inte gäller som original. Användaren ansvarar för att gällande revision används. 1(2)

Utveckling av medicinteknisk produkt Dnr: [RSMT-2026-1] Flödessplitter för högflödesgrimma VO Medicinsk teknik Skåne [Ange datum]

Digitalisering IT och MT Utveckling av medicinteknisk produkt VO Medicinsk teknik Skåne (RE) Rapport [Förtydligande dokumenttyp] [Ange datum] Dnr: [RSMT-2026-1] Anvisning: Följande formulär ska användas av ovan nämnd verksamhet i samband med: Produktframställning av medicinteknisk produkt enligt S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

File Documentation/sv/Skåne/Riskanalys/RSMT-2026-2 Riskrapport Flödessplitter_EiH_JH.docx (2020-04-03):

Riskhanteringsrapport

Flödessplitter för högflödesgrimma

Projektet omfattar följande inventarier:
Benämning: | Nummer/kod:
| 202001962, 202001973 och 202001976

Innehållsförteckning

# 1. Introduktion

Riskhanteringsrapporten är en sammanfattande rapport som skall visar att riskhanteringsplanen har följts, att kvarvarande risk är acceptabel, och att lämpliga processer för hantering av information från produktion och fält finns i enlighet med ISO 14971:2012 (1). Denna rapport ingår i Risk Management File (RMF) och hanteras som en delmängd av Design History File (DHF).

Riskhanteringsrapporten innehåller översyn av riskanalys, riskvärdering, kontroll av risker, samt utvärdering av sammantagen risk.

# 2. Produktbeskrivning

Se produktbeskrivningen (2).

# 3. Riskhanteringsprocessen

## 3.1. Riskhanteringsteam

Riskhanteringen har skötts kontinuerligt under utvecklingen, inget formellt möte har hållits utan genom löpande kontakt har risker identifierats och åtgärder genomförts. Detta är ett avsteg från processen.

Riskhanteringsteamets uppsättning finns beskrivet i Tabell 1.

Namn | Ansvar / befogenhet, avdelning
Per Nordqvist | Riskhanteringsansvarig, Medicinsk Teknik Skåne, Region Skåne
Einar Heiberg | Teknisk expertis inom 3dprint, Lunds Universitet
Jesper Hessius | ST-Läkare, Region Västmanland (Västerås)
Erik Cederberg | Teknisk expertis inom 3dprint, 3dverkstan.se
Petter Frieberg | Flödessimuleringar, Lunds Universitet
Bernborg Philip | Teknisk expertis inom 3dprint, BFT, Region Skåne
Göran Petersson | Medicinteknisk Ingenjör, Medicinsk Teknik Skåne, Region Skåne

Tabell 1 Riskhanteringsteam

## 3.2. Riskhanteringsplan

Riskhanteringen har skett enligt 133521-Riskhanteringsplan (3).

### 3.2.1. Användningsfall

Endast ett användningsfall har riskhanterats: normal användning under speciella omständigheter.

### 3.2.2. Skala för utvärdering av allvarlighet och sannolikhet

Se Appendix A.

### 3.2.3. Kriterier för att acceptera en risk

Enligt Appendix B vilket följer riskhanteringsprocessen (4).

### 3.2.4. Dokumentation

Alla dokument rörande riskanalysen skall vara en del av en ”Risk management file” (RMF), se processbeskrivningen för riskanalys (4).

## 3.3. Utvärderingsmetod, användarfall

Riskanalysen genomfördes med hjälp av användarfall som identifierades utifrån användaren och de möjliga scenarier som produkten ska stödja. Användarfallen skrevs före riskanalysmötet och användes som input under mötet. Varje steg i användarfallen diskuterades.

Användarfallen presenteras i följande tabell:

UC ID | Funktionalitet | Krav | Riskmöte
UC0 | Förutsägbar felanvändning | N/A
UC1 | Normal användning under speciella omständigheter.

Tabell 2. Användarfall

Förklaringar:

UC ID – användarfallets ID-nummer

Funktionalitet - funktionaliteten som hanteras i användningsfallet

Krav - användarkraven (URS) och produktkrav (PRS) som är relevanta för användarfallet.

Riskanalysmöte - Riskanalysmötet när användningsfallet analyserades

## 3.4. Faror

Följande faror har identifierats för produkten, se riskhanteringsschemat (5).

## 3.5. Riskvärdering

Kriterier för sannolikhet och allvarlighetsgrad som användes under riskanalysen var i enlighet med riskhanteringsplanen, efter behov blev dessa definierade i riskhanteringsschemat och finns även redovisade i Appendix A

## 3.6. Riskkontroll

Lämpliga riskkontrollåtgärder för att reducera risken till en acceptabel nivå identifierades. Riskkontrollåtgärderna dokumenterades i riskhanteringsschemat (5).

## 3.7. Införande av riskkontroll, spårbarhet

Riskkontrollåtgärderna överfördes till kravmassan i produktens kravspecifikation. Där angavs ett unikt ID enligt Produktutvecklingsprocessen (6) vilket gav en möjlighet att verifiera och spåra dessa likt andra krav.

## 3.8. Bedömning av kvarstående risker

Följande risker som kan ge upphov till patientskada finns kvar efter att riskkontrollåtgärder införts, se Tabell 3 och Tabell 4.

Risk id Ha ID [UCx.y Hx] | Risk | Riskanalys | | | Åtgärd | Återstående risk
| | Sannolikhet | Allvarlighetsgrad | Risk | | Sannolikhet | Allvarlighetsgrad | Risk
UC1 H2 - H8 | Cytotoxicity, Sensitization, Irritation, Systematic toxicity (acute), Subchronic toxicity (subacute toxicity), Genotoxicity, Implantation: Inhalation via 3D-utskrift kan ge medicinska komplikationer . Patientskada uppstår. | 4 | 3 | 12 | RK004: I kliniskt bruk endast användning av CE-märkt plast godkänd för oralt bruk (Formlabs Dental SG) | 1 | 3 | 3
UC1 H11 | Heated air: Varm fuktig luft går genom längre slangar i denna uppställning. Varm fuktig luft som möter kall yta bildar kondens. Kondensen gör att systemet tappar verkan. | 4 | 3 | 12 | RK003: Teknisk lösning i anslutning till T-koppling som samlar upp kondensvatten. | 1 | 3 | 3
UC1 H12-H13 | Bacteria och Viruses: De utskrivna komponenterna är kontaminerade. Patientskada uppstår. | 3 | 3 | 9 | RK011: utskrivna komponenterna görs i plast som tål Autoklav | 1 | 3 | 3
UC1 H15 | Bacteria: Maskinens hygien påverkar två patienter istället för en. Patientskada uppstår. | 3 | 3 | 9 | RK012: rengöring av apparat ska ske på veckobasis | 2 | 3 | 6
UC1 H16 | Incorrect or inappropriate output or functionality. Uppställningen är inte tät utan läckage uppstår. En patient får för lågt flöde vilket fördröjer behandlingen eller gör behandlingen verkningslös. | 3 | 3 | 9 | RK013: krav på täthet på konstruktionen | 1 | 3 | 3
UC1 H18 | Residues: Rester från tillverkningen kan lossna vid användningen och täppa till grimman. Patientskada uppstår | 3 | 3 | 9 | RK014: mekanisk rengöring och avsyningen på varje exemplar innan första användning. | 1 | 3 | 3
UC1 H21 | Unknown manufacturing process: Felaktiga ämnen kan komma in vid 3d-utskrift. Patientskada uppstår | 3 | 3 | 9 | RK016: processrutin för tillverkningen (utskriften) | 1 | 3 | 3

Tabell 3 Risker ≥ 8

Risk id Ha ID [UCx.y Hx] | Risk | Riskanalys | | | Åtgärd | Återstående risk
| | Sannolikhet | Allvarlighetsgrad | Risk | | Sannolikhet | Allvarlighetsgrad | Risk
UC1 H1 | Re- or cross-infection: Kondensvatten från patient A åker bakåt i flödet och hamnar i patient B's flöde. Patient B får kontaminerat kondensvatten från patient A | 2 | 3 | 6 | RK001: Avstå delad behandling av bärare av MRB RK002: Avstå delad behandling av patient med känd bakteriell sekundärinfektion(?) RK003: Teknisk lösning i anslutning till T-koppling. | 1 | 3 | 3
UC1 H9 | Incorrect or inappropriate output or functionality: Behandlingen blir ojämn på grund av att flödet delats upp. Den ena patienten får för lågt flöde vilket fördröjer behandlingen eller gör behandlingen verkningslös. | 1 | 3 | 3 | RK005: Delning endast mellan patienter med relativt lik kroppshydda RK006: Delning endast mellan patienter med samma storlek på grimma RK007: Kontroll av korrekt slang- och grimm-läge, särskilt vid upplevd försämring | 1 | 3 | 3
UC1 H10 | Incorrect or inappropriate output or functionality: Inställningarna på apparaten är svåra att justera in, detta i första hand för FiO2 då flödet bedöms ska hålla 30 lpm. Den ena patienten får för lågt flöde vilket fördröjer behandlingen eller gör behandlingen verkningslös. | 2 | 3 | 6 | RK008: Vid start av optiflow eftersträvas enskild behandling till dess att inställningar justerats RK009: Övergång till delad behandling vid stabiliserade inställningar RK010: Övergång till delad behandling till patient med samma inställningar | 2 | 3 | 6
UC1 H14 | lack of integrity of data: Patient A och B kommer behöva vara fysisk ganska nära varandra och inte i separata rum. Patientens integritet kan i viss mån kränkas. | 4 | 1 | 4 | I den mån möjligt använda skjutväggar som arrangeras för minsta möjliga insyn mellan patienter Möjlig förbättring: öka längderna på slangar ytterligare: konsekvens ej analyserad. | 4 | 1 | 4
UC1 H17 | Re- or cross-infection: Uppställningen kräver att patienter matchas, detta kan kräva förflyttning av patient bara av denna orsak. Flytt av patient kan orsaka spridning av smitta. | 2 | 3 | 6 | Vid inläggning mål om att i den mån möjligt ”matcha” patienter för potentiell samvård direkt. Bedömning från fall till fall kring behov av städning av samvårdsplats mot bakgrund av att samtliga patienter har samma smitta. | 2 | 3 | 6
UC1 H19 | Sharp edges. De tillverkade komponenterna har vassa hörn. Skada uppstår, personal eller patient | 4 | 1 | 4 | RK015: Kontroll av design av tillverkade komponenter | 1 | 1 | 1
UC1 H20 | Sunlight: Komponenter tillverkade i dentalSG kan vara känsliga för solljus. Komponent går sönder. | 2 | 2 | 4 | Blir det ett problem överväg engångs istället. | 2 | 2 | 4
UC1 H22 | Routine violation: Vid övergång från 1 till 2 patienter eller från 2 till 1 patient görs ett misstag och patient får i sig smittat kondensvatten. Patientskada uppstår | 3 | 2 | 6 | Ingen åtgärd annan än skriftlig rutin. | 3 | 2 | 6

Tabell 4 Risker < 8 och allvarligheten är ≥ 1

## 3.9. Risk / nyttoanalys

Produkten får endast används inom häls- och sjukvården inom Region Skåne.

Behandling med högflödessyrgas anses avgörande vid Covid-19 och kan rädda från intubation. I det kritiska läge sjukvården är i och med Covid-19 2020 har denna möjlighet att dubblera behandlingskapaciteten tagits fram. De risker som identifierats är väl dokumenterade och åtgärder är genomförda. Riskerna ska vägas gentemot den nytta behandlingen gör för den enskilda patienten. Metoden att dela högflöde ska inte ersätta en behandling med en apparat per patient utan ska bara användas i de fall den möjligheten inte finns.

# 4. Summering av riskhanteringen

## 4.1. Dokumenthantering

Denna rapport och dokument som krävs för riskhanteringen skall bevaras i Risk Management File. Ansvarig för riskhanteringen i projektet säkrar att detta sker.

## 4.2. Riskhantering under Produktion och livscykelhantering

Riskhantering skall fortsätta enligt de beslut som gäller denna produkt av en produktansvarig. Återkoppling på produkten och användningen av den sker till: FoU.mt@skane.se.

# 5. Referenser

1. ISO 14971:2012, Medicintekniska produkter – Tillämpning av ett system för riskhantering för medicintekniska produkter.

2. SPEC-200331 Produktbeskrivning Flödessplitter.

3. ST_LIST-133021 Riskhanteringsplan.

4. PROC-10014, Processbeskrivning Riskhantering.

5. 133023 Riskhanteringsschema - Flödessplitter.

6. PROC-10011, Processbeskrivning Produktutveckling.

7. ISO 13485:2012, Medicintekniska produkter – Ledningssystem för kvalitet – Krav för regulatoriska ändamål.

8. ISBN:978-91-86301-28-6, Riskanalys & Händelseanalys - handbok för patientsäkerhet.

9. IEC 62366, Medical devices - Application of usibility engineering to medical devices.

# 6. Revisionshistorik

Version | Datum | Versionsförändring av | kommentar
0.1 | 200402 | Per Nordqvist | Första version av dokumentet på nytt nummer

# Appendix A Kriterier för allvarlighetsgrad och sannolikhet

Allvarlighetsgrad / poäng | Exempel på konsekvenser
Katastrofal / 4 | Dödsfall/självmord Bestående stor funktionsnedsättning (sensorisk, motorisk, fysiologisk, intellektuell eller psykologisk)
Betydande / 3 | Bestående måttlig funktionsnedsättning (sensorisk, motorisk, fysiologisk, intellektuell eller psykologisk) Förlängd vårdepisod för tre eller fler patienter Förhöjd vårdnivå för tre eller fler patienter
Måttlig / 2 | Övergående funktionsnedsättning (sensorisk, motorisk, fysiologisk, intellektuell eller psykologisk) Förlängd vårdepisod för en eller två patienter Förhöjd vårdnivå för en eller två patienter
Mindre / 1 | Obehag eller obetydlig skada
Obetydlig / 0 | Ingen skada

Tabell 5, Skala för bedömning av allvarlighetsgrad

Sannolikhet / poäng | Förekomst / Vanlighet
Mycket stor / 4 | Kan inträffa varje dag
Stor / 3 | Kan inträffa varje vecka
Liten / 2 | Kan inträffa varje månad
Mycket liten / 1 | Kan inträffa 1gång/ 1-2 år
Obefintlig / 0 | Uppträder aldrig

Tabell 6, Skala för bedömning av sannolikhet

Om faran kommer från ett mjukvarusystem ska sannolikheten antas vara 100%.

# Appendix B Riskvärdering

Genom att multiplicera värdet för allvarlighetsgraden med värdet för sannolikhet erhålls riskens storlek: Allvarlighetsgrad X Sannolikhet = Riskens storlek

| | Allvarlighetsgrad
| | Katastrofal / 4 | Betydande / 3 | Måttlig / 2 | Mindre / 1 | Obetydlig / 0
Sannolikhet | Mycket stor / 4 | 16 | 12 | 8 | 4 | 0
| Stor / 3 | 12 | 9 | 6 | 3 | 0
| Liten / 2 | 8 | 6 | 4 | 2 | 0
| Mycket liten / 1 | 4 | 3 | 2 | 1 | 0
| Obefintlig / 0 | 0 | 0 | 0 | 0 | 0

Tabell 7, riskvärderingstabell

Rött i riskanalysen | Risker som får riskpoäng 8 eller högre ska analyseras och åtgärdas. | Färgmarkera riskvärdet rött i kolumnen ”Risk”
Orange i riskanalysen | Om en risk får riskpoäng mellan 4 ska analysteamet avgöra om risken ska analyseras och åtgärdas. Om allvarlighetsgraden är 4 ska det övervägas om risken ska analyseras och åtgärdas oavsett sannolikhet. | Färgmarkera riskvärdet gult i kolumnen ”Risk”
Gult i riskanalysen | Risker där sannolikheten beror på mjukvara och där allvarlighetsgraden är större än 1, ska analyseras och åtgärdas. För risker där sannolikheten beror på mjukvara och där allvarlighetsgraden är 0 eller 1, ska analysteamet avgöra om risken analyseras och åtgärdas. | Färgmarkera riskvärdet orange i kolumnen ”Risk”
Blått i riskanalysen | Nya faror identifierade efter att en åtgärd införts eller om utvärdering av återstående risk ger att risken inte är acceptabel. | Färgmarkera riskvärdet blått i kolumnen ”Ha id”

\\RSFS083\Hem6$\181806\_Dokument\Egentillverkning\0_Covid-19\Flödessplitter\Teknisk fil\RSMT-2026-2 Riskrapport Flödessplitter.docx 13-3525 Original lagras elektroniskt, observera att utskrivet dokument inte gäller som original. Sid Användaren ansvarar för att gällande revision används. 13(13)

Region Skåne Digitalisering IT och MT Medicinsk teknik Skåne Organisationsnummer 291 89 Kristianstad Lasarettsgatan 37, 221 85 Lund 232100-0255 Original lagras elektroniskt, observera att utskrivet dokument inte gäller som original. Användaren ansvarar för att gällande revision används. 1(13)

Utveckling av medicinteknisk produkt Dnr: RSMT 2026-2 Delat högflöde VO Medicinsk teknik Skåne 2020-04-02

Digitalisering IT och MT Utveckling av medicinteknisk produkt VO Medicinsk teknik Skåne (RE) Rapport [Förtydligande dokumenttyp] [Ange datum] Dnr: RSMT 2026-2 Anvisning: Följande formulär ska användas av ovan nämnd verksamhet i samband med: Produktframställning av medicinteknisk produkt enligt SOS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

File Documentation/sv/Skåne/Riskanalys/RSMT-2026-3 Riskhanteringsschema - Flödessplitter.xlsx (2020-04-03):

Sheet: Hazard ID and Checklist
Hazard ID and checklist
ID | Hazards | Applicable | Applicable Hazards: | Analysed
H1 | Heated air |  | Unknown manufacturing process.
H2 | Inadequate specification of accessories to be used with the medical device |  | Bacteria | x
H3 | Unknown manufacturing process. | x | Viruses
H4 | Operator with lower ability |  | Residues | x
H5 | Incorrect alarm |  | Incorrect or inappropriate output or functionality | x
H6 | Routine violation | x | Sharp edges | x
H7 | Moving of patient |  | Cytotoxicity | x
H8 | Line voltage |  | Sensitization | x
H9 | Enclosure leakage current |  | Irritation or intracutaneous reactivity | x
H10 | Earth leakage current |  | Routine violation | x
H11 | Patient leakage current |  | Sunlight | x
H12 | Interference with other equipment
H13 | Electric fields
H13-1 | Ionizing radiation |  | Re- or cross-infection | x
H13-2 | Non-ionizing radiation |  | Heated air | x
H14 | Magnetic fields |  | lack of integrity of data | x
H15 | High temperature, emitted | x | Systematic toxicity (acute) | x
H16 | Low temperature, emitted |  | Subchronic toxicity (subacute toxicity) | x
H17 | Gravity falling | x | Genotoxicity | x
H18 | Gravity Suspended masses |  | Implantation | x
H19 | Vibration
H20 | Stored energy
H21 | Moving parts
H22 | Torsion, shear and tensile force
H23 | Sunlight
H24 | Acoustic sound energy
H25 | High pressure fluid injection
H26 | Bacteria | x
H27 | Viruses | x
H28 | Re- or cross-infection | x
H29 | Exposure of airway, tissues, environment or property, e.g. to foreign materials.
H30 | Acids or alkalis
H31 | Residues | x
H32 | Contaminates
H33 | Lack of calibration
H34 | Additives or processing aids
H35 | Cleaning, disinfecting or testing agents
H36 | Degradation products
H37 | Toxicity of chemical constituents - allergenicity/irritancy
H38 | Toxicity of chemical constituents - pyrogenicity
H39 | Incorrect or inappropriate output or functionality | x
H40 | Incorrect measurement
H41 | Erroneous data transfer
H42 | Loss or deterioration of function
H43 | Software error | x
H44 | Attentional failure
H44-1 | Memory failure
H44-2 | Rule-based failure
H44-3 | Knowledge-based failure
H45 | X-ray
H46 | Medicicnes or medical gasses
H47 | Anaesthetic products
H48 | Incomplete instructions for use
H49 | Inadequate description of performance characteristics
H50 | Inadequate specification of intended use
H51 | Inadequate disclosure of limitations
H52 | Inadequate specification of pre-use checks
H53 | Aged components
H54 | Over-complicated operating instructions
H55 | Warnings of side effects
H56 | Warnings of hazards likely with re-use of single-use medical devices
H57 | Specification of service and maintenance
H57-1 | Lack of Service or maintenence
H58 | Tissue pressure
H59 | Cooling media
H60 | Cold environment
H61 | Hot environment
H62 | Software virus
H63 | Mechanical forces | x
H64 | Re-use (multiple)
H65 | Material characteristics
H66 | Unintended use (misuse)
H67 | Environmental influences (salt water, sand)
H68 | Environment (slippery surfaces, obstacles)
H69 | Sharp edges | x
H70 | Fire
H71 | Small objects
H72 | Detachable parts
H73 | Pressurized media
H74 | Anatomy out of expected range | x
H75 | Poor user interface
H76 | Insufficient training
H77 | Anaesthetic products
H78 | Smell
H79 | Packaging issues
H80 | Degradation of mechanical integrity
H81 | Uncontrolled Changes
H82 | Unstable process (not manufacturing related)
H83 | Biocompatibility issues
H83-1 | Cytotoxicity | x
H83-2 | Sensitization | x
H83-3 | Irritation | x
H83-4 | Systemic toxicity
H83-5 | Subchronic toxicity
H83-6 | Genotoxicity
H83-7 | Implantation
H83-8 | Hemocompatibility issues
H84 | Insertion procedure
H85 | Dislodgement of device
H86 | Dosage
H87 | Pinch
H88 | Noise
H89 | Lack of clinical evaluation
H89-1 | Not all risks have been addressed by the clinical evaluation
H89-2 | Not all relevant clinical literature has been included.
H89-3 | Clinically relevant data was accidentally excluded.
H90 | Bone splinter
H91 | Fumes
H92
 | SOFTWARE specific Hazards (from 60601-1):
 | undesired feedback [physical and data] (possibilities include: unsolicited input, out of range or inconsistent input, and input originating from electromagnetic interference)
 | unavailable data
 | lack of integrity of data
 | incorrect data
 | incorrect timing of data
 | unintended interactions within and among PESS
 | unknown aspects or quality of third-party software
 | unknown aspects or quality of third-party PESS
 | lack of data security, including its effects on data privacy, and particularly vulnerability to tampering, unintended interaction with other programs and viruses
 | failure of the IT NETWORK
 | Authentication of user

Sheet: Risk acceptans
S; Severity of Harm
Rating | General Definition | Product specific Definition | Value
Catastrophic | Results in detah or permanent impairment or life-threatening injury Bestående stor funktionsnedsättning (sensorisk, motorisk, fysiologisk, intellektuell eller psykologisk) | 4 Död | 4
 |  |  | 4
 |  | 4 bestående stor funktionsnedsättning | 4
 |  |  | 4
Critical | Bestående måttlig funktionsnedsättning (sensorisk, motorisk, fysiologisk, intellektuell eller psykologisk) Förlängd eller förhöjd vårdepisod för tre eller fler patienter |  | 3
 |  | 3 förlängd vårdepisod tre eller fler patienter | 3
 |  |  | 3
Serious | Results in injury or impairment requiring professional medical intervention Förlängd eller förhöjd vårdepisod för en eller två patienter |  | 2
 |  | 2 förlängd vårdepisod en eller två patienter | 2
 |  | 2 skärsår, större | 2
 |  | 2 fysiskt våld från patient | 2
 |  | 2 skada som kräver läkarvård | 2
 |  |  | 2
Minor | Obehag eller obetydlig skada Results in temporary injury or impairment not requiring professional medical intervention | 1 mindre skärsår eller liknande | 1
 |  | 1 obehag eller liknande | 1
 |  | 1 Bakteriell/virus smitta, hud | 1
Negligble | Ingen skada |  | 0
 |  | 0 ingen skada | 0
 |  | 0 Utebliven bedömning | 0
 |  | 0 Merarbete för personal | 0
 |  |  |  | S
Po; Probability of occurence of Harm
Definition | Probability (1/XXX) |  | Value
Frequent
Probable
Occasional
Unusual
Remote
Improbable
Beräkningarna görs på maximal användning inom Region Skåne för Covid-19: 100 apparater delas till 200 patienter.
 | Katastrofal / 4 | Dödsfall/självmord
 |  | Bestående stor funktionsnedsättning (sensorisk, motorisk, fysiologisk, intellektuell eller
 |  | psykologisk)
 | Betydande / 3 | Bestående måttlig funktionsnedsättning (sensorisk, motorisk, fysiologisk, intellektuell eller psykologisk)
 |  | Förlängd vårdepisod för tre eller fler patienter
 |  | Förhöjd vårdnivå för tre eller fler patienter
 | Måttlig / 2 | Övergående funktionsnedsättning (sensorisk, motorisk, fysiologisk, intellektuell eller psykologisk)
 |  | Förlängd vårdepisod för en eller två patienter
 |  | Förhöjd vårdnivå för en eller två patienter
 | Mindre / 1
 | Obetydlig / 0 | Ingen skada
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

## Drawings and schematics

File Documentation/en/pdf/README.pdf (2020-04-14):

README.md - SHFNO.org | Updated on: 4/14/2020

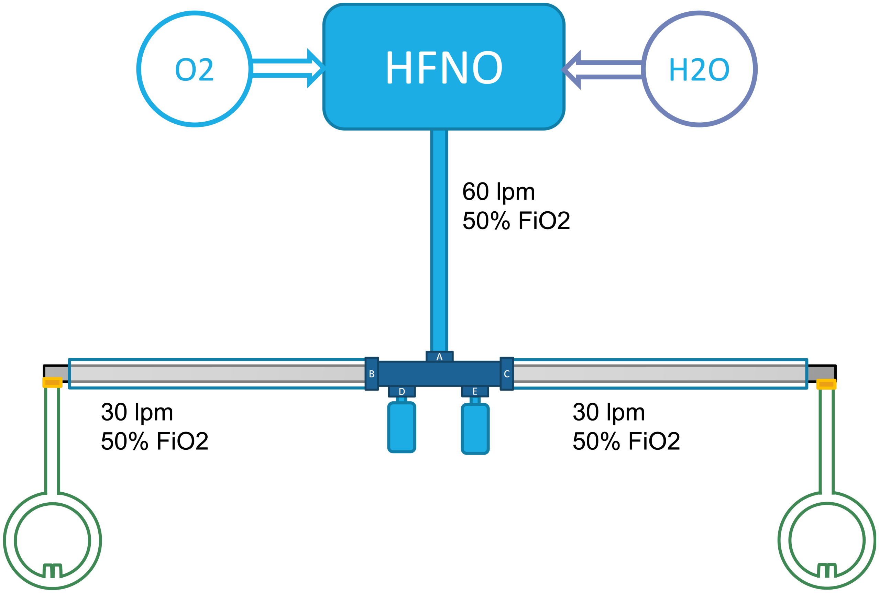
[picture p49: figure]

1 / 2

# Welcome to the HFNOsplitter project - SHFNO.org

This project is dedicated to doubling the capacity for High Flow Nasal Oxygen (HFNO) treatment by simultaneously connecting two COVID-19 patients to one HFNO-device by adding 3D printed parts. We also provide thorough medical instructions, validation, and risk analysis to enable other healthcare providers to adopt Split HFNO (SHFNO). This project is currently only aimed at the Airvo™ 2 Optiflow™ system (Fisher & Paykel Healthcare Limited, Berkshire, United Kingdom).

Fig 1. SHFNO Schematic setup

N.B. 1This solution is providedas is with no express or implied warranty. Providedunder the CERN-OHL-Slicense. In no event will the authorsbe heldliable for anydamages arising from the use of this (https://github.com/hessius/HFNOsplitter/blob/master/LICENSE_cern_ohl_s_v2.pdf) solution. Legal notice.

N.B. 2This project is notdone in conjuction or collaboration with, nor under the influence of the original manufacturer of any equipment, medical or otherwise.

## Working group

Jesper Hessius

MD, Internal Medicine and Cardiology Resident, Västmanland Hospital Västerås Region Västmanland
Role: Project initiator - Project coordinator - Documentation - Risk analysis

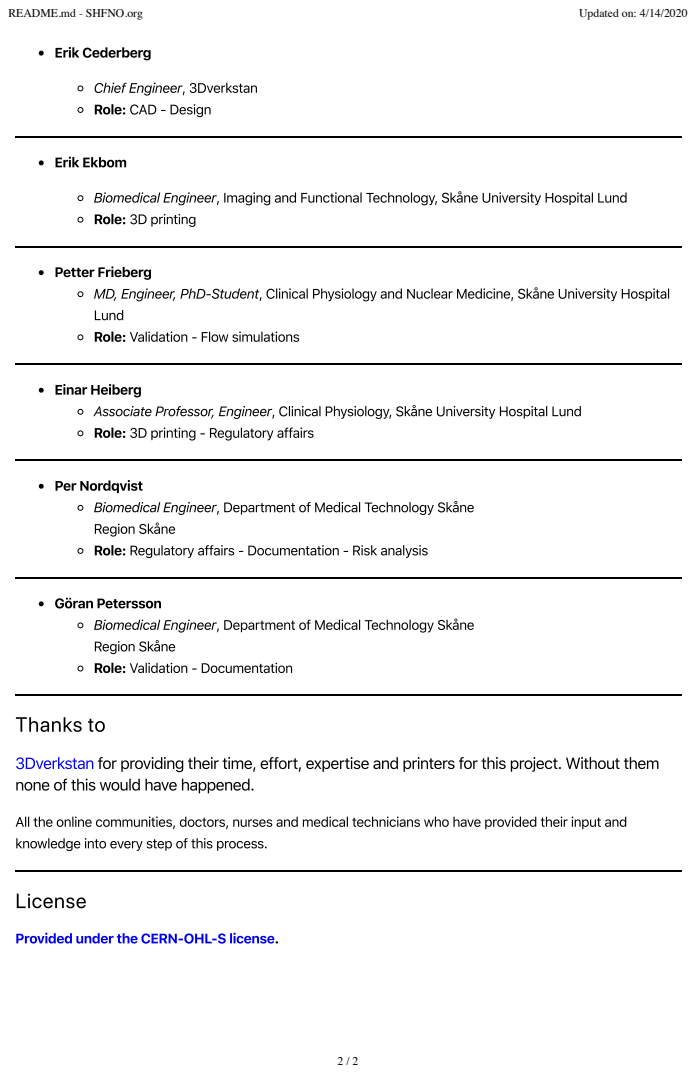
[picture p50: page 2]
README.md - SHFNO.org; Updated on: 4/14/2020; Erik Cederberg; Erik Ekbom; Thanks to; License

Chief Engineer, 3Dverkstan
Role: CAD - Design

Biomedical Engineer, Imaging and Functional Technology, Skåne University Hospital Lund
Role: 3D printing

Petter Frieberg
MD, Engineer, PhD-Student, Clinical Physiology and Nuclear Medicine, Skåne University Hospital
Lund
Role: Validation - Flow simulations

Einar Heiberg
Associate Professor, Engineer, Clinical Physiology, Skåne University Hospital Lund
Role: 3D printing - Regulatory affairs

Per Nordqvist
Biomedical Engineer, Department of Medical Technology Skåne
Region Skåne
Role: Regulatory affairs - Documentation - Risk analysis

GöranPetersson
Role: Validation - Documentation

3Dverkstan (http://3dverkstan.se/) for providing theirtime, effort, expertise and printers forthis project. Withoutthem
none ofthis would have happened.

All the online communities, doctors, nurses and medical technicians who have provided theirinput and
knowledge into every step of this process.

Providedunder the CERN-OHL-Slicense. (https://github.com/hessius/HFNOsplitter/blob/master/LICENSE_cern_ohl_s_v2.pdf)

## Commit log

2020-04-02 Add 3D files
    [Optiflow-Adapter.stl]
2020-04-03 File updates
    [RSMT-2026-3 Riskhanteringsschema - Flödessplitter.xlsx]
2020-04-03 Update models
    [Adapter.stl, Airvo-F-22-F.stl, Airvo-F-22-M-V2.stl, Airvo-M-22-F.stl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]
2020-04-03 Directory Name Change
    [Adapter.stl, Airvo-F-22-F.stl, Airvo-F-22-M-V2.stl, Airvo-M-22-F.stl]
2020-04-05 Add final documentation items
    [Airvo-F-22-M.stl, Airvo-M-22-M.stl]
2020-04-08 Rename STL files
    [AirSpiral-15mm.stl, AirSpiral-22mm.stl, Optiflow-15mm.stl, Optiflow-22mm.stl]
2020-04-08 Add file changelog, update files, update sw instructions
    [Plug-15mm.stl, Plug-PET.stl]
2020-04-08 Reorg + Update instructions
    [Plug-15mm.stl, Plug-PET.stl]
2020-04-09 Update with guideline references, new files and naming
    [Adapter-AirSpiral-15mm.stl, Adapter-AirSpiral-22mm.stl, Adapter-Optiflow-15mm.stl, Adapter-Optiflow-22mm.stl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]
2020-04-12 Name Changes
    Name Changes to better reflect Male/Female couplings.
    [Adapter-AirSpiral-22mm-F.stl, Adapter-AirSpiral-22mm-M.stl, Adapter-Optiflow-22mm-F.stl, Adapter-Optiflow-22mm-M.stl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]
2020-04-13 Combi mount version, both ISO and zip tie added
2020-04-13 Changed main version to combi-mount
